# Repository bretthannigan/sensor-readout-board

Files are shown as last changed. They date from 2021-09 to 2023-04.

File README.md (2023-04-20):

# Sensor Readout Board

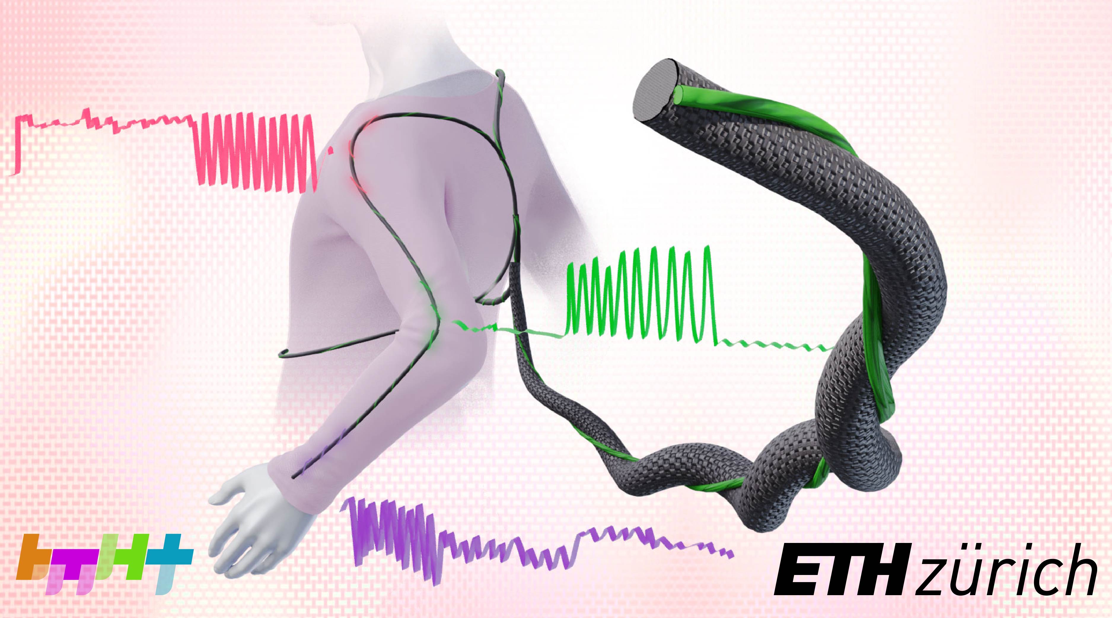
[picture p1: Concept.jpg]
Concept image


This repository includes the software, firmware, and hardware for the readout electronics used in the paper:

> B. C. Hannigan, T. J. Cuthbert, C. Admadizadeh, and C. Menon, _Distributed Sensing Along Fibres for Smart Clothing_. April 2023. [Preprint]

## Python Client

The `Client` subfolder contains the source code for the PC client, written in Python. The client allows connection to the FPGA and optional logging of data. The data can be interpreted in a variety of formats, such as:
- `raw`: raw ADC counts (32-bit signed integer)
- `iq`: impedances expressed as in-phase and quadrature components (equivalently, real and imagingary impedance components) in Ohms.
- `magphase`: impedances expressed as magnitude (in dB) and phase (in degrees).
- `RCseries`: impedances converted to resistance and capacitance values in an RC series circuit.
- `RCparallel`: impedances converted to resistance and capacitance values in an RC parallel circuit.
- `model`: (experimental) processed signals using a provided model (e.g., from sklearn or Keras) to convert the raw signals into a measure of interest.
Command-line arguments exist to control the COM port and logfile destination. One can also enable or disable the plotting of data to the screen and triggering ability. Note that the correct gain that matches the jumper on the PCB must be supplied via command-line argument for the scaling to be correct. There also exist some calibration curves as Excel spreadsheets.

## FPGA Firmware

The `Firmware` folder contains many general-purpose logic buliding blocks such as counters, FIFOs, memories, etc. and associated test-benches. The `Firmware/top` subfolder contains the top-level Verilog file `top.v` which was used for the data collection in the paper. This relies directly on the following third-party libraries:
- `verilog-lfsr` by Alex Forencich: https://github.com/alexforencich/verilog-lfsr. Used to implement the linear-feedback shift register that enables redundancy checking for the MIN protocol serial packets.
- `osdvu/uart` by Timothy Goddard: https://github.com/cyrozap/osdvu. Used to implement the UART.
- `min-protocol` by Ken Tindell: https://github.com/min-protocol/min. Used to frame the data sent to the PC.

## Hardware

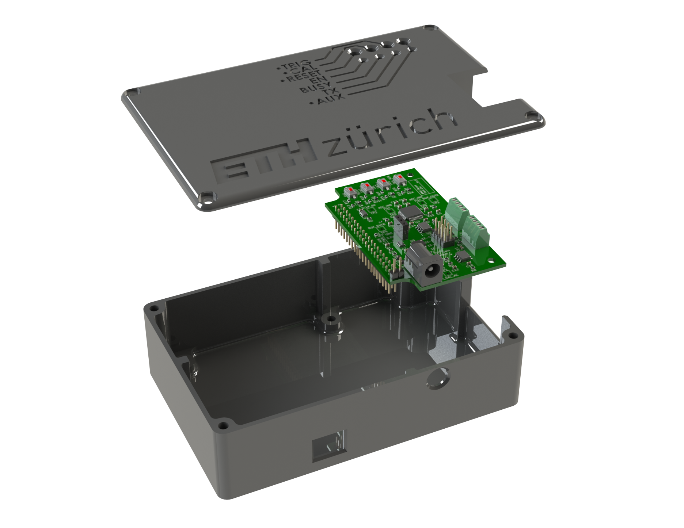
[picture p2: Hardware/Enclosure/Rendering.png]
Hardware rendering


The `Hardware/Enclosure` subfolder contains Solidworks files for the system enclosure. These were printed on a FDM 3D printer. The `Hardware/PCB` subfolder contains PCB schematic and layout files from KiCAD. The other subfolders contain (disorganized) SPICE simulations, previous iterations, and other files used during development.

©2023 ETH Zurich, Brett Hannigan; D-HEST; Biomedical and Mobile Health Technology (BMHT) Lab; Carlo Menon

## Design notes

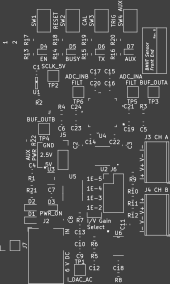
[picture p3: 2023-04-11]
Hardware/PCB/SensReadPCB-F_SilkS.png

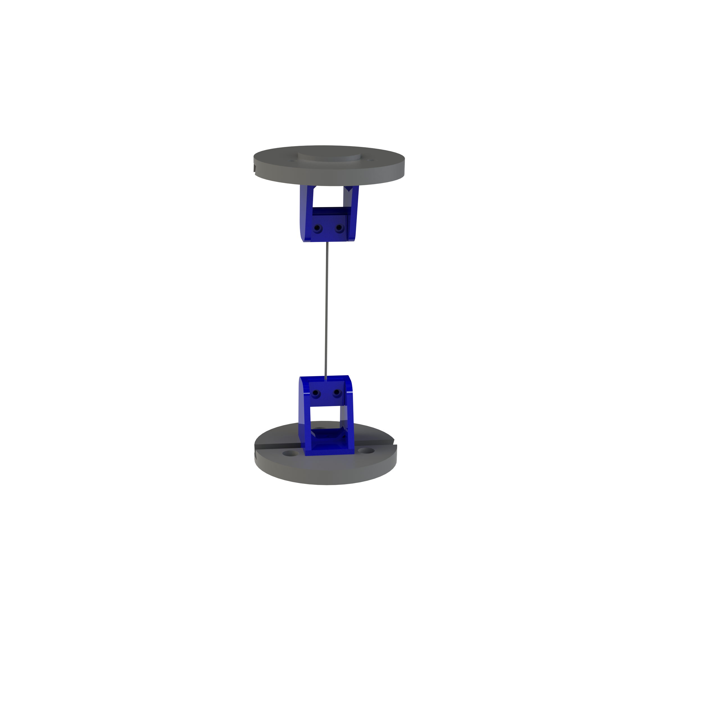
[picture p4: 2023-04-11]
Hardware/Enclosure/Single Sensor.png

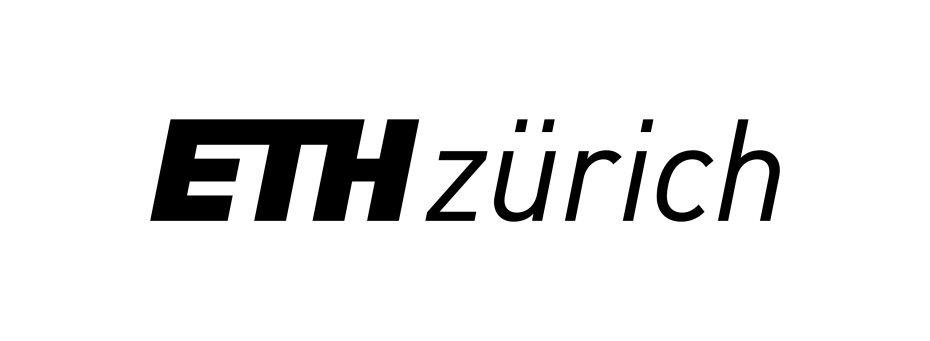
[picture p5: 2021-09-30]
Hardware/PCB/ethz.png

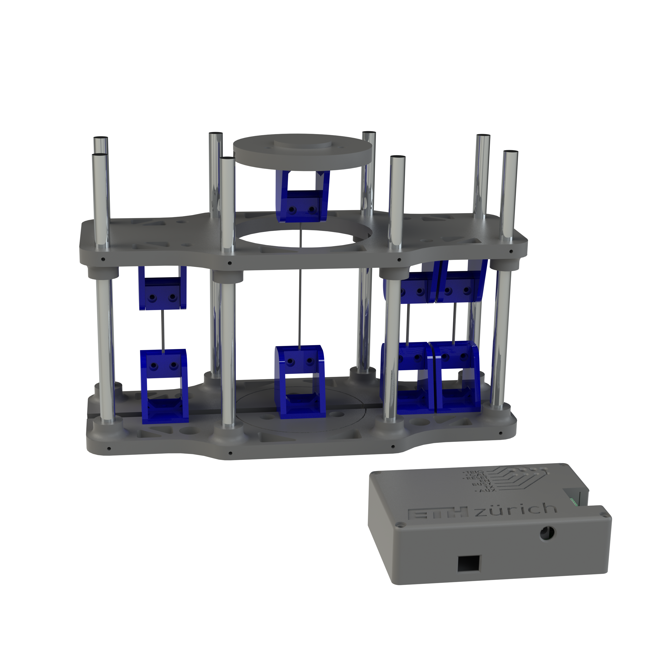
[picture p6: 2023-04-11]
Hardware/Enclosure/Rendering with Readout Enclosure.png

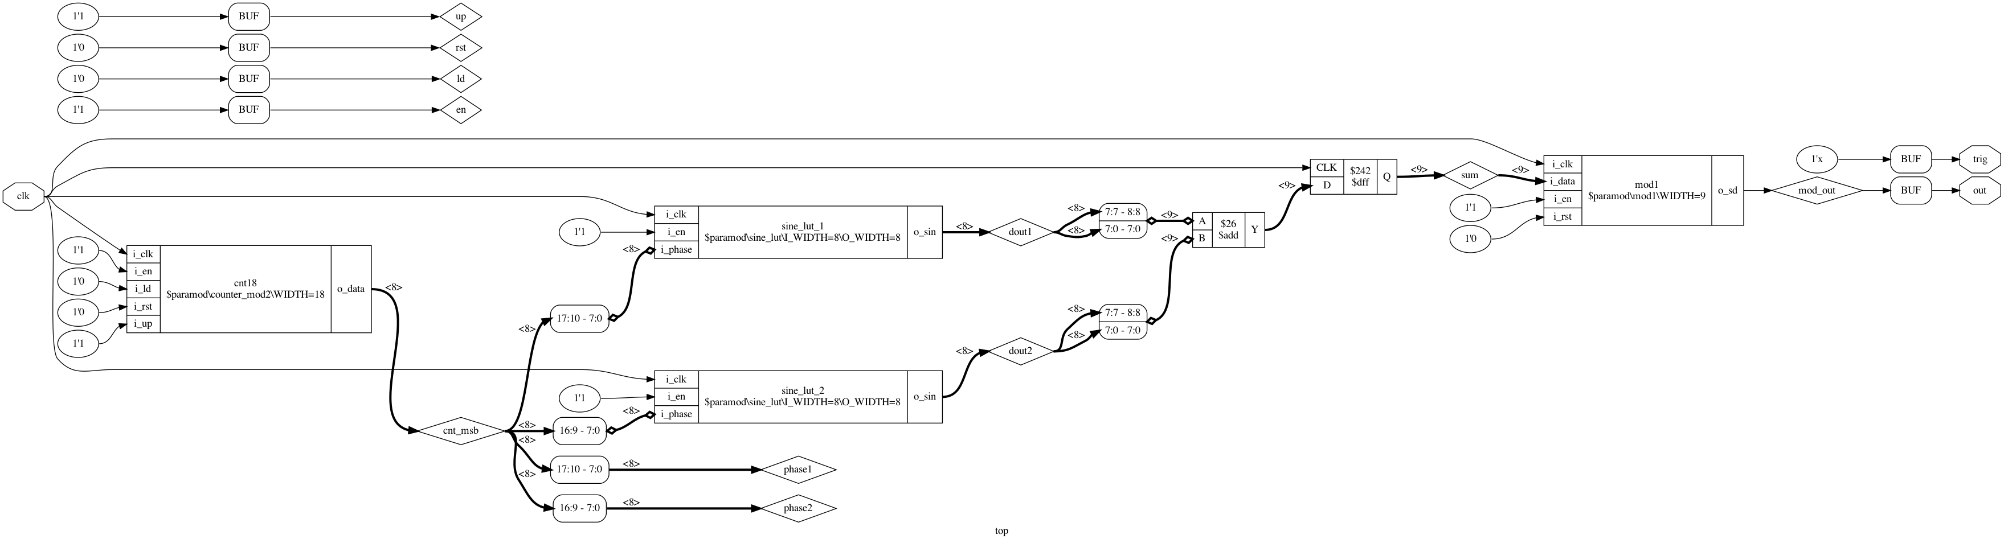
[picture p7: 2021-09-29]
Firmware/top/top.png

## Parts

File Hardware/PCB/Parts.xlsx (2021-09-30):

Electronics Assembly Product Order |  |  |  |  | 2021-09-24
Quantity | Retailer | Category | Product | Purpose | Price (ea.)
2 | Distrelec.ch | General lab | Drawer Cabinet, 36.3kg, 306x150x552mm, Raaco (https://www.distrelec.ch/en/drawer-cabinet-36-3kg-306x150x552mm-raaco-1240-123/p/18001510?q=&pos=4&origPos=4&origPageSize=50&track=true) | Parts bin organizer for electronic components. | 67.10 CHF
1 | Distrelec.ch | General lab | Precision Tweezers, Pointed, Stainless Steel 140mm, Weller Erem (https://www.distrelec.ch/en/precision-tweezers-pointed-stainless-steel-140mm-weller-erem-sssa/p/30186113) | Tweezers for general use | 17.99 CHF
1 | Distrelec.ch | General lab | SMD Tweezers, Stainless Steel, 45° Angled, 115mm, Ideal Tek (https://www.distrelec.ch/en/smd-tweezers-stainless-steel-45-angled-115mm-ideal-tek-sm103-sa/p/30101939) | Tweezers for SMD assembly | 22.83 CHF
2 | Distrelec.ch | General lab | Antistatic Adjustable Hypoallergenic Wrist Strap 10mm, Blue, RND Lab (https://www.distrelec.ch/en/antistatic-adjustable-hypoallergenic-wrist-strap-10mm-blue-rnd-lab-rnd-560-00208/p/30130388?q=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) | ESD grounding for assembly | 2.77 CHF
2 | Distrelec.ch | General lab | Coiled Earth Lead 3.05m, RND Lab (https://www.distrelec.ch/en/coiled-earth-lead-05m-rnd-lab-rnd-600-00094/p/30131945?q=&pos=3&origPos=3&origPageSize=50&track=true) | ESD grounding for assembly | 4.24 CHF
 |  |  |  |  | 189.04 CHF

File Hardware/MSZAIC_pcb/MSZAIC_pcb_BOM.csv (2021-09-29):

Reference | Value | Footprint | Datasheet | Done
U1 | LMH6619MA_NOPB | LMH6619MA:LMH6619MA&slash_NOPB |  | TRUE
R1 | 100k | Resistors_SMD:R_1206_HandSoldering | ~ | TRUE
R2 | 100k | Resistors_SMD:R_1206_HandSoldering | ~ | TRUE
R3 | 10k | Resistors_SMD:R_1206_HandSoldering | ~ | TRUE
C1 | 20p | Capacitors_SMD:C_1206_HandSoldering | ~ | TRUE
R4 | 10k | Resistors_SMD:R_1206_HandSoldering | ~ | TRUE
C2 | 20p | Capacitors_SMD:C_1206_HandSoldering | ~ | TRUE
J3 | Conn_02x04_Odd_Even | Pin_Headers:Pin_Header_Straight_2x04_Pitch2.54mm | ~ | TRUE
R5 | 10k | Resistors_SMD:R_1206_HandSoldering | ~ | TRUE
R6 | 1k | Resistors_SMD:R_1206_HandSoldering | ~ | TRUE
R7 | 100 | Resistors_SMD:R_1206_HandSoldering | ~ | TRUE
R8 | 10 | Resistors_SMD:R_1206_HandSoldering | ~ | TRUE
C9 | 100n | Capacitors_SMD:C_1206_HandSoldering | ~ | TRUE
U4 | TLE2426xD | TLE2426CD:TLE2426CD | http://www.ti.com/lit/ds/symlink/tle2426.pdf | TRUE
C11 | 1u | Capacitors_SMD:C_1206_HandSoldering | ~ | TRUE
U3 | LP2985A-10DBVR | LP2985A10DBVR:LP2985A-10DBVR |  | TRUE
C6 | 1u | Capacitors_SMD:C_1206_HandSoldering | ~ | TRUE
C10 | 10n | Capacitors_SMD:C_1206_HandSoldering | ~ | TRUE
C7 | 10n | Capacitors_SMD:C_1206_HandSoldering | ~ | TRUE
U2 | MAX903CSA+ | MAX903CSA:MAX903CSA&plus_ |  | TRUE
C4 | 100n | Capacitors_SMD:C_1206_HandSoldering | ~ | TRUE
C8 | 100n | Capacitors_SMD:C_1206_HandSoldering | ~ | TRUE
C5 | 100n | Capacitors_SMD:C_1206_HandSoldering | ~ | TRUE
C3 | 100n | Capacitors_SMD:C_1206_HandSoldering | ~ | TRUE
TP1 | DAC_AC | Measurement_Points:Measurement_Point_Square-TH_Big | ~ | #N/A
R16 | 6.98k | Resistors_SMD:R_1206_HandSoldering | ~ | TRUE
R14 | 4.64k | Resistors_SMD:R_1206_HandSoldering | ~ | TRUE
R15 | 1.10k | Resistors_SMD:R_1206_HandSoldering | ~ | TRUE
C13 | 1.5n | Capacitors_SMD:C_1206_HandSoldering | ~ | TRUE
TP6 | ADC_OUT | Measurement_Points:Measurement_Point_Square-TH_Big | ~ | #N/A
J1 | Barrel_Jack | Connectors:BARREL_JACK | ~ | TRUE
R19 | 510 | Resistors_SMD:R_1206_HandSoldering | ~ | TRUE
D4 | PWR_ON | LEDs:LED_1206_HandSoldering | ~ | TRUE
D1 | D_Schottky | Diodes_SMD:D_1206 | ~ | TRUE
D3 | D_Schottky | Diodes_SMD:D_1206 | ~ | TRUE
D6 | D_Zener | Diodes_SMD:D_1206 | ~ | TRUE
R18 | 1k | Resistors_SMD:R_1206_HandSoldering | ~ | TRUE
D2 | D_Zener | Diodes_SMD:D_1206 | ~ | TRUE
D5 | ENABLE | LEDs:LED_1206_HandSoldering | ~ | TRUE
R17 | 68 | Resistors_SMD:R_1206_HandSoldering | ~ | TRUE
R24 | 28k | Resistors_SMD:R_1206_HandSoldering | ~ | #N/A
R27 | 28k | Resistors_SMD:R_1206_HandSoldering | ~ | #N/A
C14 | 130p | Capacitors_SMD:C_1206_HandSoldering | ~ | #N/A
C16 | 130p | Capacitors_SMD:C_1206_HandSoldering | ~ | #N/A
R25 | 1.58meg | Resistors_SMD:R_1206_HandSoldering | ~ | #N/A
C15 | 130p | Capacitors_SMD:C_1206_HandSoldering | ~ | #N/A
R26 | 68.1k | Resistors_SMD:R_1206_HandSoldering | ~ | #N/A
R23 | 5.11k | Resistors_SMD:R_1206_HandSoldering | ~ | #N/A
C17 | 390p | Capacitors_SMD:C_1206_HandSoldering | ~ | #N/A
TP5 | LF_4 | Measurement_Points:Measurement_Point_Square-TH_Big | ~ | #N/A
R20 | 0R | Resistors_SMD:R_1206_HandSoldering | ~ | TRUE
R21 | 0R | Resistors_SMD:R_1206_HandSoldering | ~ | TRUE
R22 | 0 | Resistors_SMD:R_1206_HandSoldering | ~ | TRUE
R29 | 0 | Resistors_SMD:R_1206_HandSoldering | ~ | TRUE
R28 | 5.36k | Resistors_SMD:R_1206_HandSoldering | ~ | TRUE
C20 | 100n | Capacitors_SMD:C_1206_HandSoldering | ~ | TRUE
C18 | C | Capacitors_SMD:C_1206_HandSoldering | ~
TP4 | LF_3 | Measurement_Points:Measurement_Point_Square-TH_Big | ~ | #N/A
RV2 | 47k | 23BR50KLFTR:23BR50KLFTR | ~ | TRUE
C19 | 100n | Capacitors_SMD:C_1206_HandSoldering | ~ | TRUE
R10 | 13.7k | Resistors_SMD:R_1206_HandSoldering | ~ | TRUE
TP3 | LF_2 | Measurement_Points:Measurement_Point_Square-TH_Big | ~ | #N/A
TP2 | LF_1 | Measurement_Points:Measurement_Point_Square-TH_Big | ~ | #N/A
RV1 | 10k | 23BR50KLFTR:23BR50KLFTR | ~ | TRUE
R13 | 806 | Resistors_SMD:R_1206_HandSoldering | ~ | TRUE
R12 | 750 | Resistors_SMD:R_1206_HandSoldering | ~ | TRUE
R11 | 14.0k | Resistors_SMD:R_1206_HandSoldering | ~ | TRUE
C12 | 680p | Capacitors_SMD:C_1206_HandSoldering | ~ | TRUE
R9 | 4.75k | Resistors_SMD:R_1206_HandSoldering | ~ | TRUE
U5 | LM6144AIM_NOPB | LM6144AIM:LM6144AIM&slash_NOPB |  | TRUE
TP8 | TestPoint | Measurement_Points:Measurement_Point_Square-TH_Big | ~ | #N/A
TP7 | TestPoint | Measurement_Points:Measurement_Point_Square-TH_Big | ~ | #N/A
J4 | Screw_Terminal_01x04 | TerminalBlocks_Phoenix:TerminalBlock_Phoenix_MPT-2.54mm_4pol | ~ | TRUE
J2 | Conn_02x20_Odd_Even | Pin_Headers:Pin_Header_Straight_2x20_Pitch2.54mm | ~ | TRUE
 |  |  |  | 56

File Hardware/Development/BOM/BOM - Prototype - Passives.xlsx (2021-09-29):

Howland Current Source
Label | Type | Value
R1 | Resistor | 100 kΩ | *must be matched
R2 | Resistor | 100 kΩ | *must be matched
R3 | Resistor | 10 kΩ | **must be matched
R4 | Resistor | 10 kΩ | **must be matched
C1 | Capacitor | 20 pF
C2 | Capacitor | 20 pF
ADC Stage 1
Label | Type | Value
R1 | Resistor | 56.2 kΩ
R2 | Resistor | 90 kΩ
R3 | Resistor | 261 kΩ
R4 | Resistor | 2.32 kΩ
R5 | Resistor | 2.47 kΩ
R6 | Resistor | 95.3kΩ
R7 | Resistor | 16.5 kΩ
R8 | Resistor | 280 kΩ
C1 | Capacitor | 200 pF
C2 | Capacitor | 200 pF
ADC Stage 2
Label | Type | Value
R1 | Resistor | 1.58 MΩ
R2 | Resistor | 5.36 kΩ
R3 | Resistor | 5.11 kΩ
R4 | Resistor | 68.1kΩ
R5 | Resistor | 28 kΩ | *must be matched
R6 | Resistor | 28 kΩ | *must be matched
C1 | Capacitor | 390 pF
C2 | Capacitor | 130 pF
C3 | Capacitor | 130 pF | **must be matched
C4 | Capacitor | 130 pF | **must be matched
Extras
Decoupling capacitors 100 nF
Various test resistances, 100 Ω - 50 kΩ
Various test capacitors in the pF range

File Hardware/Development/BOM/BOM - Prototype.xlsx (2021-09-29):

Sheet: Sheet1
Howland Current Source
Label | Type | Value/Part Number
R1 | Resistor | 100 kΩ | *must be matched | l
R2 | Resistor | 100 kΩ | *must be matched | l
R3 | Resistor | 10 kΩ | **must be matched | l
R4 | Resistor | 10 kΩ | **must be matched | l
C1 | Capacitor | 20 pF |  | l
C2 | Capacitor | 20 pF |  | l
U1 | Op-amp | OPA350PA |  | l
U2 | Op-amp | OPA350PA |  | l
U3 | Voltage reference | TLE2426CP |  | l
ADC Loop filter
Label | Type |  | Value
R1 | Resistor |  | 14.0 kΩ | l
R2 | Resistor |  | 1.10 kΩ | l
R3 | Resistor |  | 4.64 kΩ | l
R4 | Resistor |  | 4.75 kΩ | l
R5 | Resistor |  | 6.98 kΩ | l
R6 | Resistor |  | 13.7 kΩ | l
R7 | Resistor |  | 750 Ω | l
R8 | Resistor |  | 806 Ω | l
C1 | Capacitor |  | 680 pF
C2 | Capacitor |  | 1.5 nF
Extras
Decoupling capacitors 100 nF |  |  |  | l
Various test resistances, 100 Ω - 50 kΩ |  |  |  | l
Various test capacitors in the pF range |  |  |  | l

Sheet: 2021-02-04
ADC Loop filter | Stage 1
Label | Type | Value | Ordered | Notes
R1 | Resistor | 11.3k | TRUE
R2 | Resistor | 11.8k | TRUE
R3 | Resistor | 9.09k | TRUE
R4 | Resistor | 9.76k | TRUE
R5 | Resistor | 24.9k | TRUE
R6 | Resistor | 16.2k | TRUE
R7 | Resistor | 2.61k | TRUE
R8 | Resistor | 5.11k | TRUE
C1 | Capacitor | 160p | TRUE | 150p instead
C2 | Capacitor | 160p | TRUE | 150p instead
ADC Loop filter | Stage 2
Label | Type | Value | Ordered | Notes
R1 | Resistor | 243k | TRUE
R2 | Resistor | 5.23k | TRUE
R3 | Resistor | 1.30k | TRUE
R4 | Resistor | 46.4k | TRUE
R5 | Resistor | 5.62k | TRUE
R6 | Resistor | 5.62k | TRUE
C1 | Capacitor | 220p | TRUE
C2 | Capacitor | 22p | TRUE
C3 | Capacitor | 100p | TRUE
C4 | Capacitor | 100p | TRUE
Missed from last order
R13 | Resistor | 806 | TRUE

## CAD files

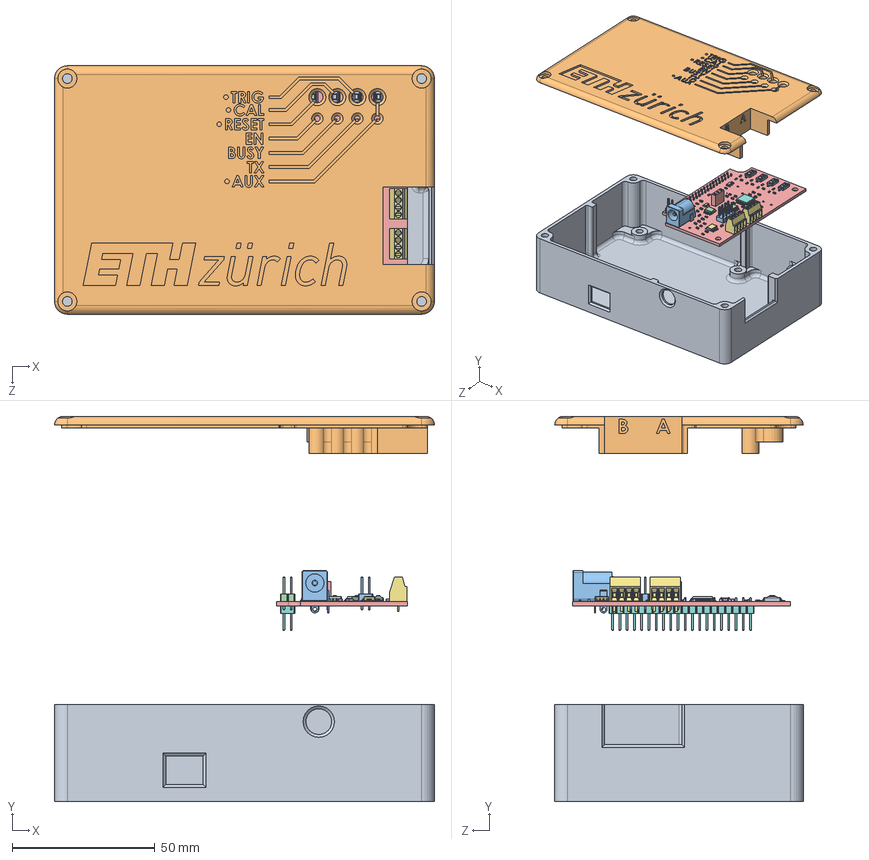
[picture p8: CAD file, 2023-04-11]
Hardware/Enclosure/Enclosure.SLDASM
133.0 x 134.9 x 87.0 mm
EnclosureBase
EnclosureLid
SOLID.step x 2
SOLID-0.step
SOLID-1.step
SOLID-2.step x 24
SOLID-3.step x 2
SOLID-4.step
SOLID-5.step x 22
SOLID-6.step x 5
SOLID-7.step
SOLID-8.step
COMPOUND.step
COMPOUND-9.step
COMPOUND-10.step
COMPOUND-11.step
COMPOUND-12.step x 4
COMPOUND-13.step
SOLID-14.step
COMPOUND-15.step
COMPOUND-16.step

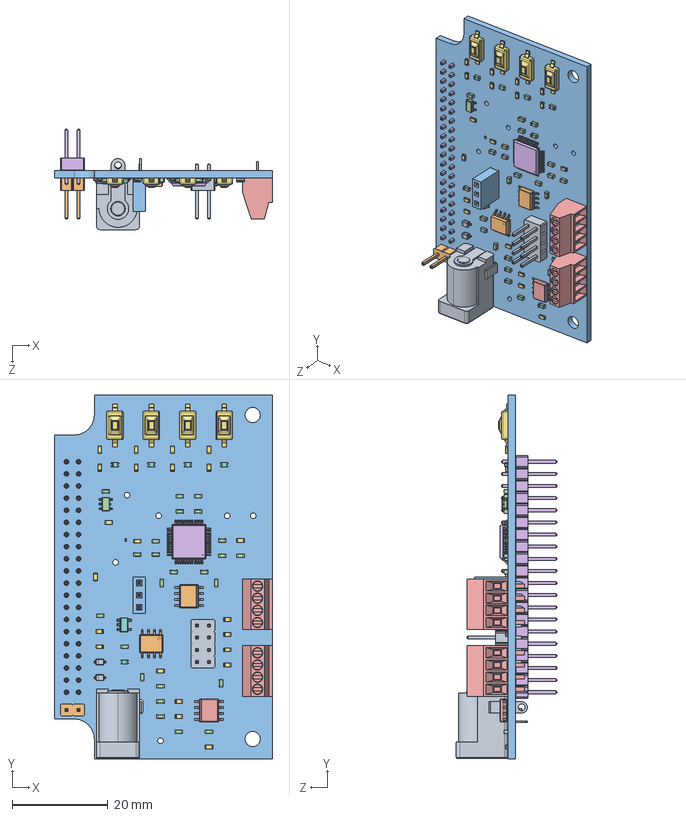
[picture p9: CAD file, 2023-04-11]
Hardware/Enclosure/SensReadPCB.SLDASM
45.7 x 76.2 x 21.0 mm
SOLID.step x 2
SOLID-0.step
SOLID-1.step
SOLID-2.step x 24
SOLID-3.step x 2
SOLID-4.step
SOLID-5.step x 22
SOLID-6.step x 5
SOLID-7.step
SOLID-8.step
COMPOUND.step
COMPOUND-9.step
COMPOUND-10.step
COMPOUND-11.step
COMPOUND-12.step x 4
COMPOUND-13.step
SOLID-14.step
COMPOUND-15.step
COMPOUND-16.step

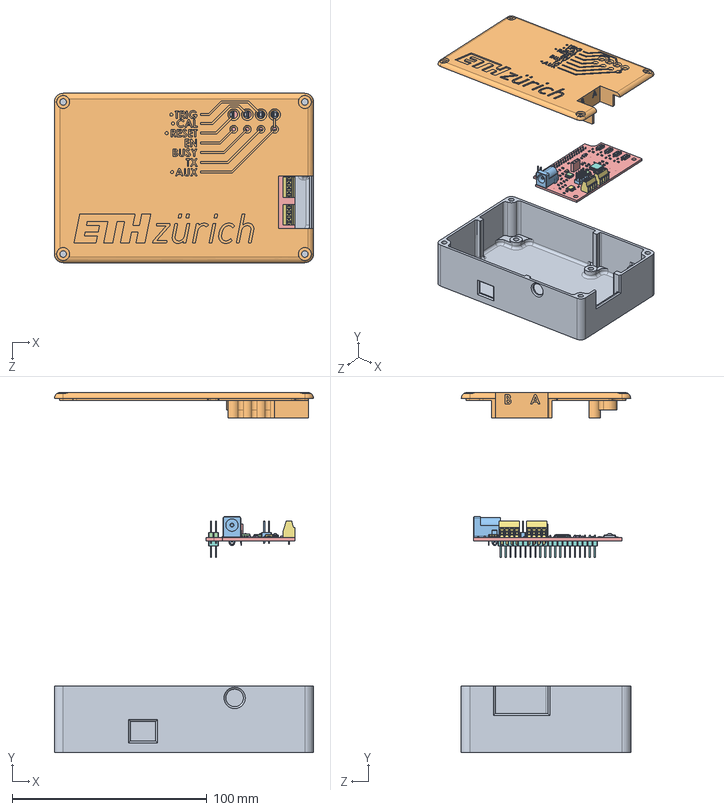
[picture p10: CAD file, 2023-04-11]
Hardware/Enclosure/Backup of Enclosure.SLDASM
133.0 x 184.7 x 87.0 mm
EnclosureBase
EnclosureLid
SOLID.step x 2
SOLID-0.step
SOLID-1.step
SOLID-2.step x 24
SOLID-3.step x 2
SOLID-4.step
SOLID-5.step x 22
SOLID-6.step x 5
SOLID-7.step
SOLID-8.step
COMPOUND.step
COMPOUND-9.step
COMPOUND-10.step
COMPOUND-11.step
COMPOUND-12.step x 4
COMPOUND-13.step
SOLID-14.step
COMPOUND-15.step
COMPOUND-16.step

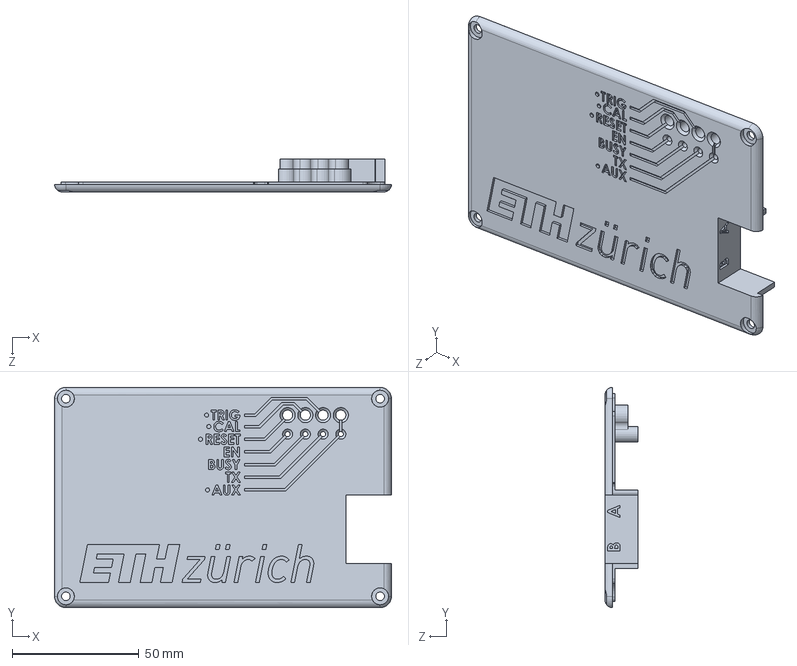
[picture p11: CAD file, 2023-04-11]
Hardware/Enclosure/EnclosureLid.sldprt
133.0 x 87.0 x 13.0 mm

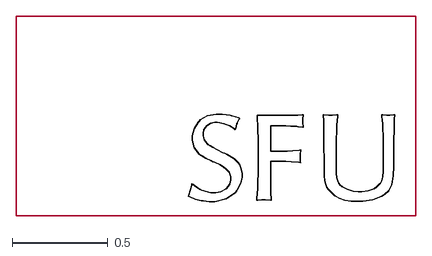
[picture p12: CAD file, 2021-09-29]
Hardware/MSZAIC_pcb/SFU-block-logo.dxf
2.08 x 1.04

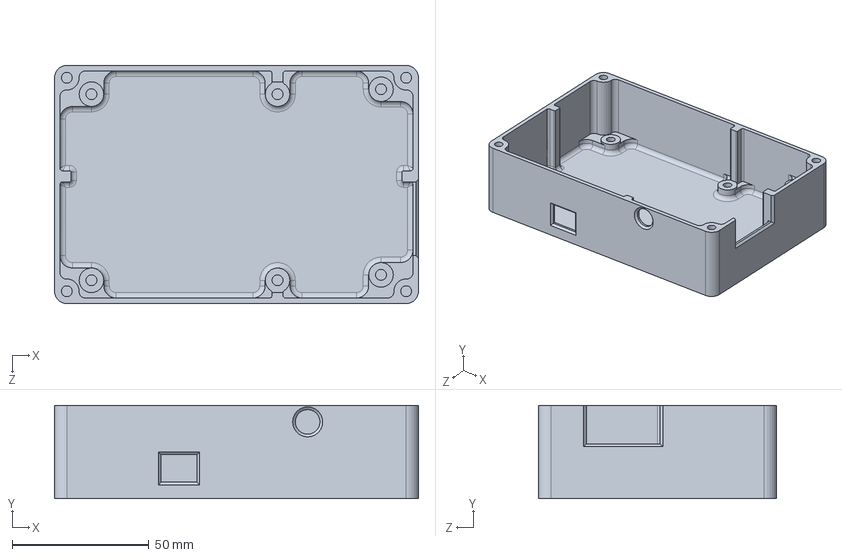
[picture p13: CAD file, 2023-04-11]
Hardware/Enclosure/EnclosureBase.SLDPRT
133.0 x 34.0 x 87.0 mm

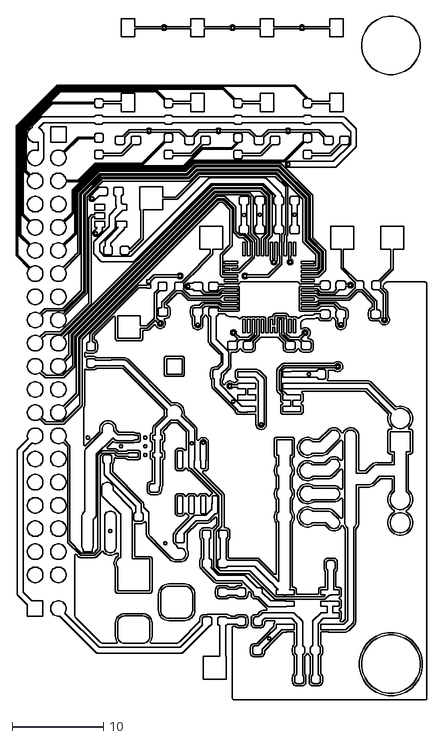
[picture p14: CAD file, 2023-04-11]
Hardware/PCB/SensReadPCB-F_Cu.dxf
45.0 x 74.9

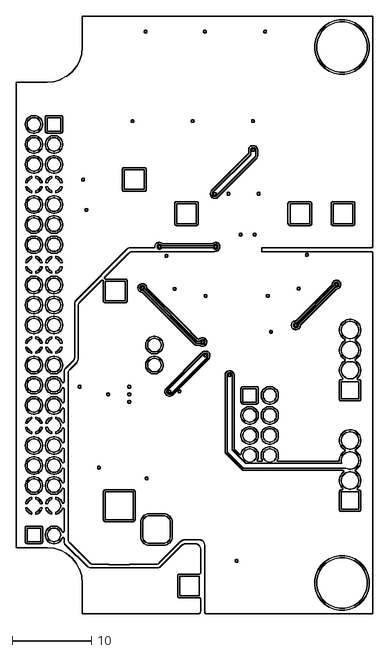
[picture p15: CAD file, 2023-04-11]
Hardware/PCB/SensReadPCB-B_Cu.dxf
45.2 x 75.6

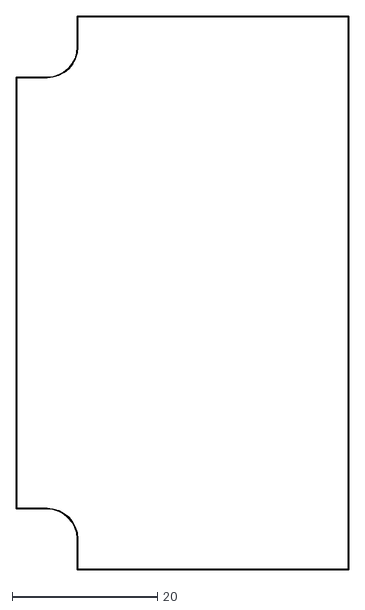
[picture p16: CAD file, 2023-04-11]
Hardware/PCB/SensReadPCB-Edge_Cuts.dxf
45.8 x 76.3

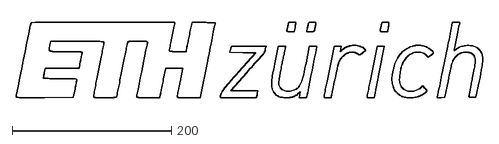
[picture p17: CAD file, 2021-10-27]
Hardware/Enclosure/ethz.dxf
584.9 x 95.1

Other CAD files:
Firmware/sine_lut/sintable.obj
Hardware/PCB/sensreadpcb.wrl_2.sldprt
Hardware/PCB/SensReadPCB.FCStd
Hardware/Enclosure/EnclosureLid - EnclosureBase-1.STL
Hardware/Enclosure/EnclosureLid - EnclosureLid-1.STL
Hardware/Enclosure/BH1BoardEnclosure.STL
Hardware/Enclosure/BH2EnclosureBase.STL
Hardware/Enclosure/Backup of EnclosureLid.sldprt
Hardware/Enclosure/BH3EnclosureLid.STL
Hardware/Enclosure/BH4EnclosureLid.STL
Hardware/Enclosure/Backup of EnclosureBase.SLDPRT
Hardware/Enclosure/EnclosureBase.SLDDRW
Hardware/PCB/SensReadPCB-B_Mask.dxf
Hardware/PCB/SensReadPCB-B_Paste.dxf
Hardware/PCB/SensReadPCB-B_SilkS.dxf
Hardware/PCB/SensReadPCB-F_Mask.dxf
Hardware/PCB/SensReadPCB-F_Paste.dxf

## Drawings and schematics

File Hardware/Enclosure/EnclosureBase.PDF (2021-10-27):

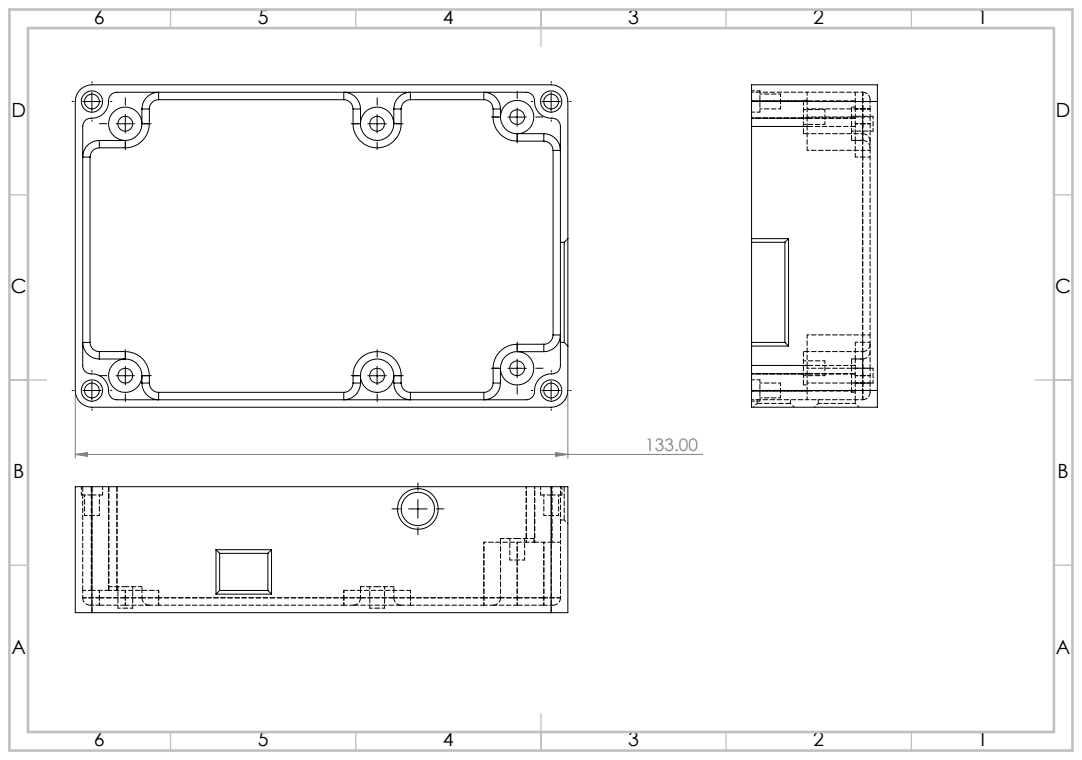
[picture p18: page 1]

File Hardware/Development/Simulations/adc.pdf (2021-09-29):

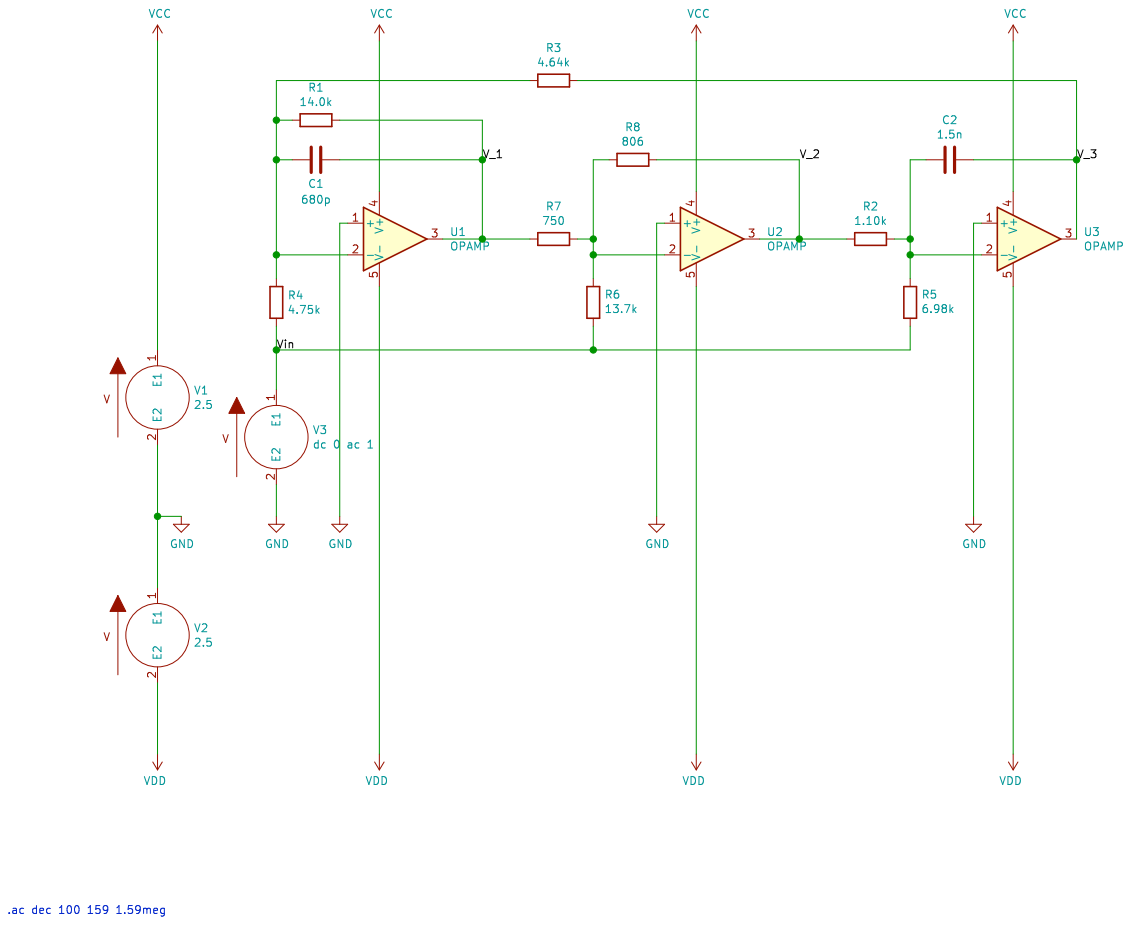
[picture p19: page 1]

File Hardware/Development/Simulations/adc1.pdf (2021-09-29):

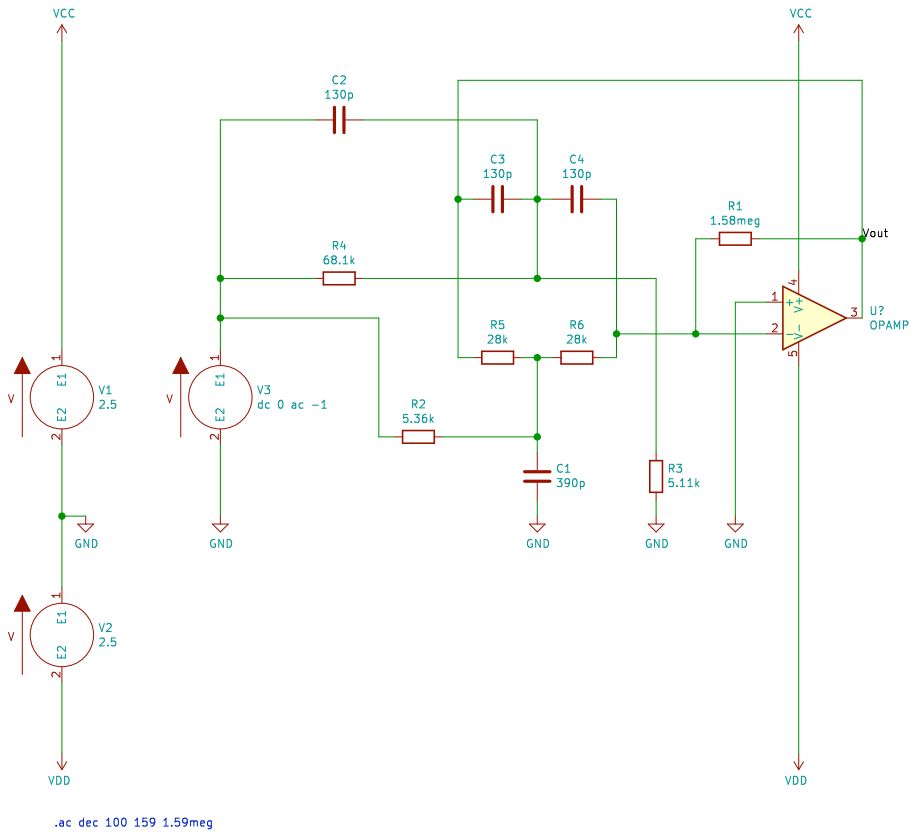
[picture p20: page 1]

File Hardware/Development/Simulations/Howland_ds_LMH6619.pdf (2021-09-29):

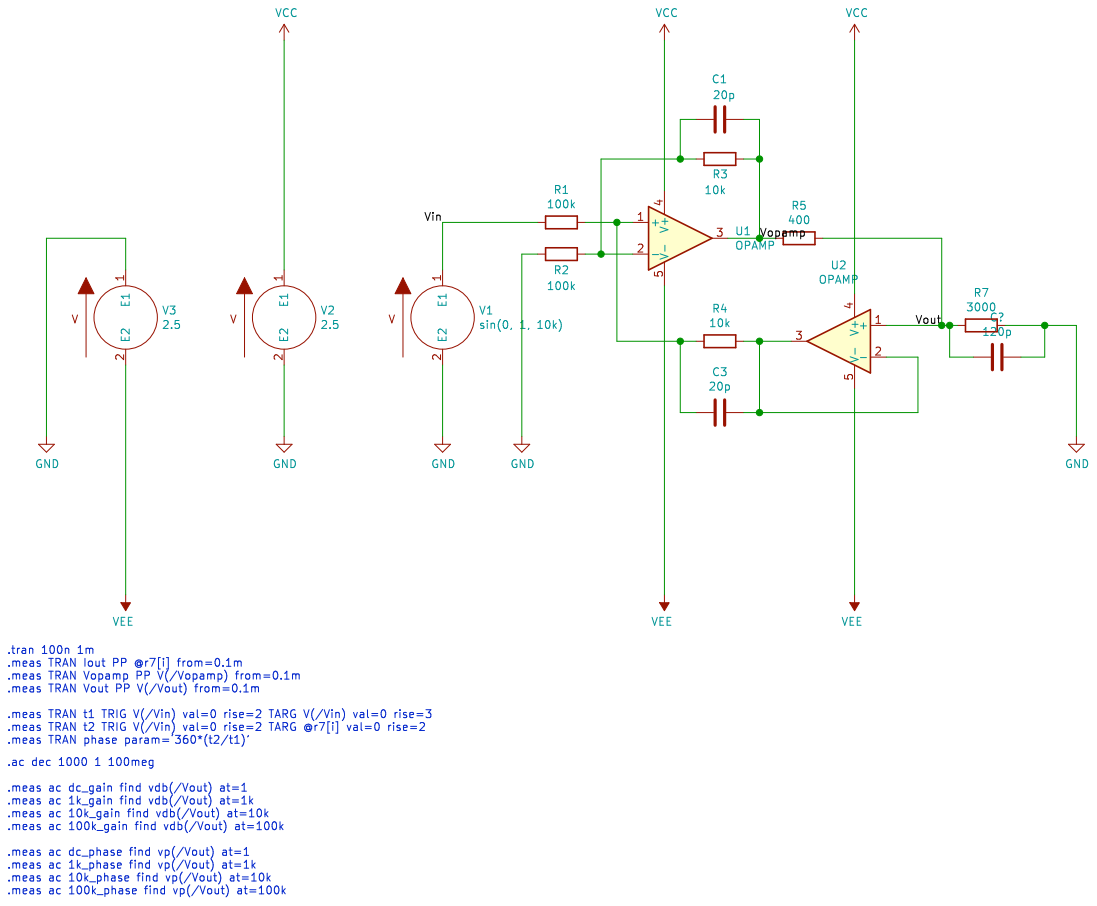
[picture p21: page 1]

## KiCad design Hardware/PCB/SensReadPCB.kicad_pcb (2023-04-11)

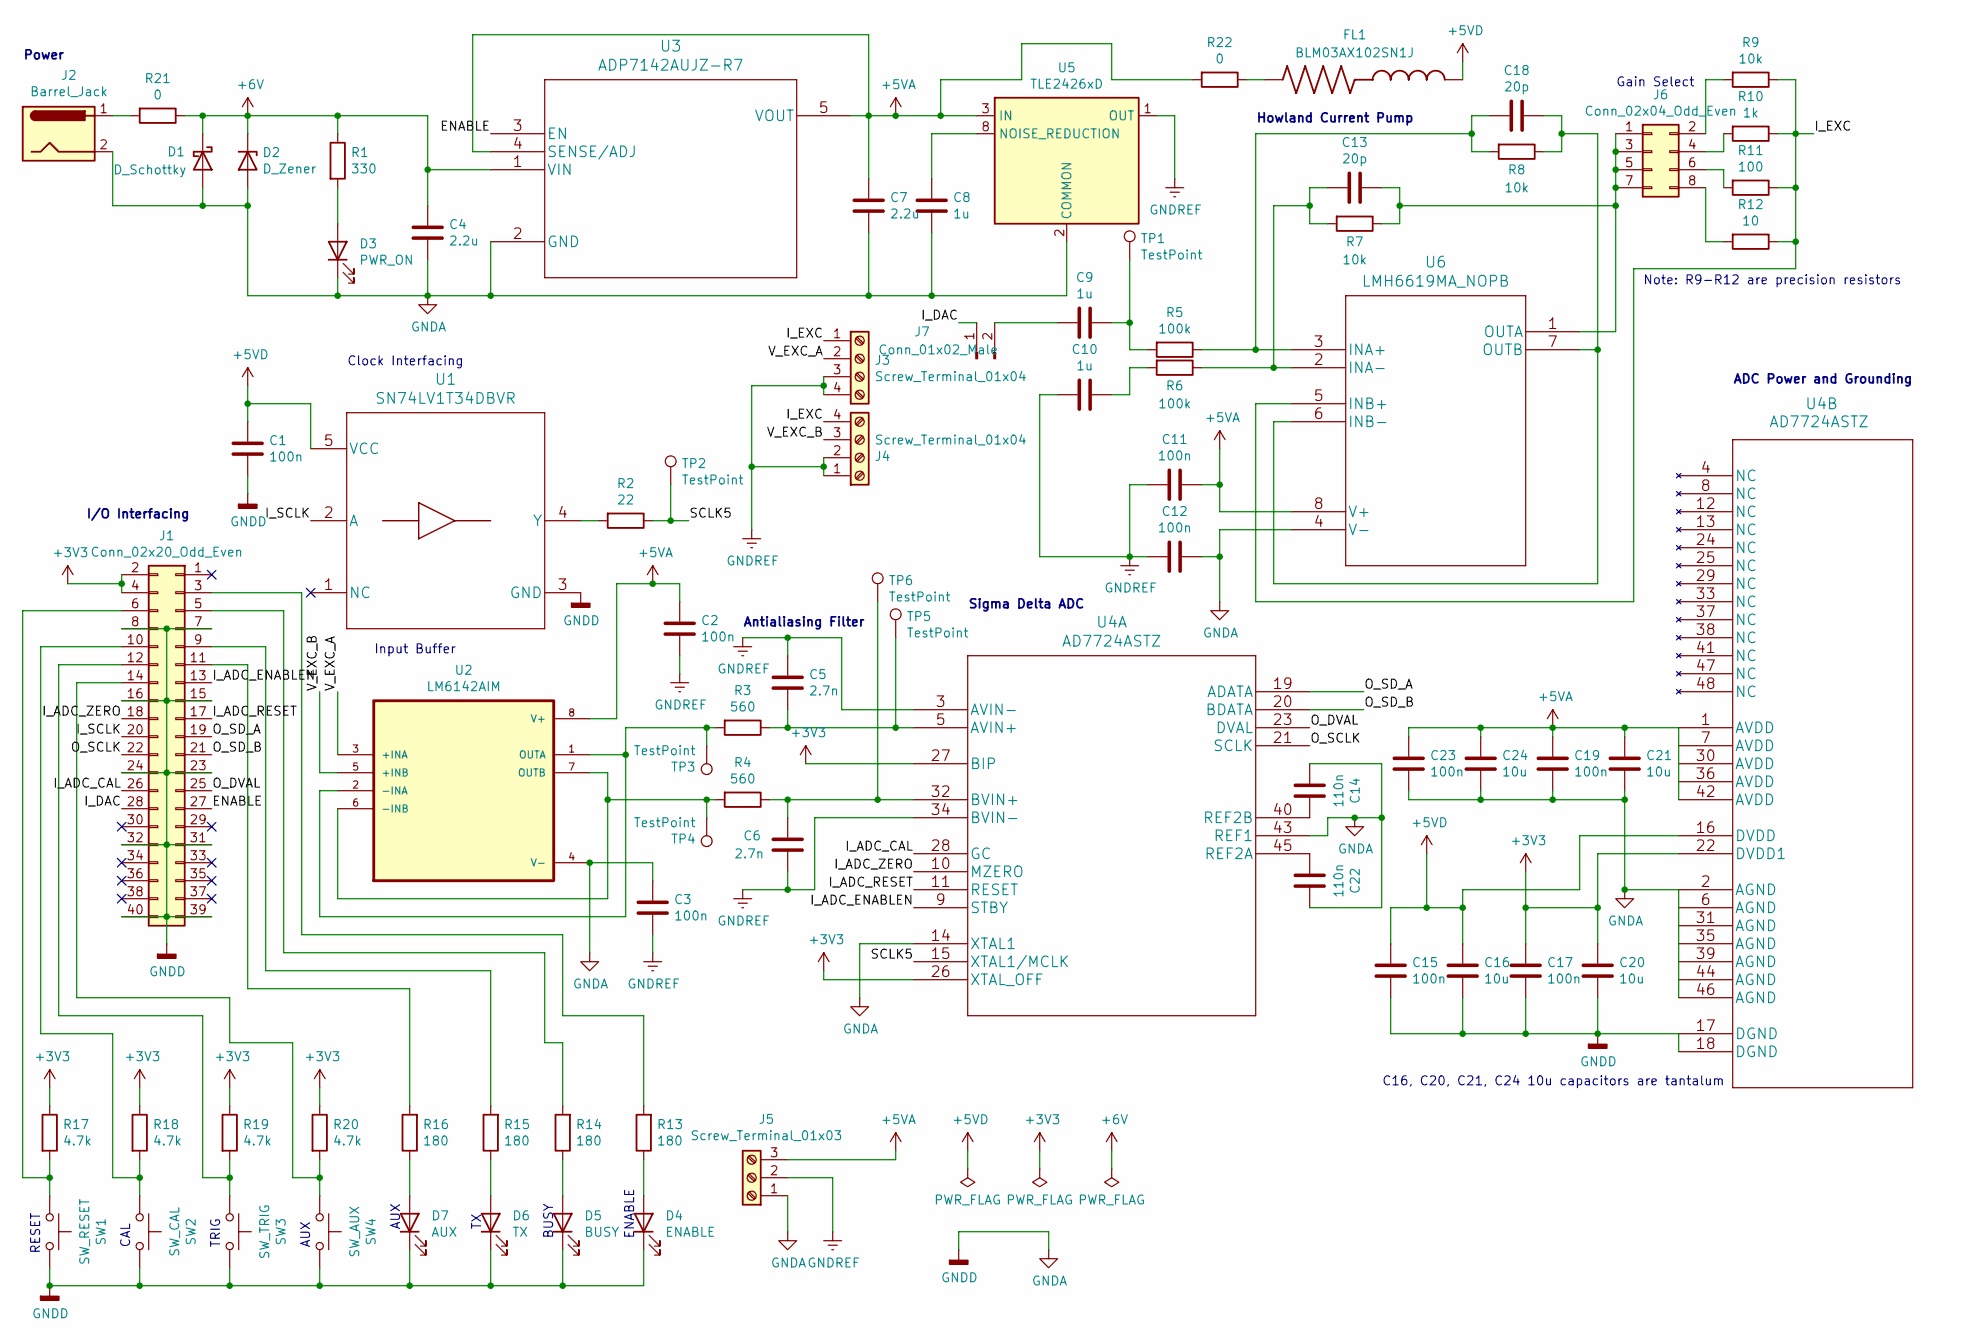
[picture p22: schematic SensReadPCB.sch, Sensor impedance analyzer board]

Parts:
C1, C2, C3, C11, C12, C15, C17, C19, C23: 100n; C_0603_1608Metric_Pad1.08x0.95mm_HandSolder
C4, C7: 2.2u; C_0603_1608Metric_Pad1.08x0.95mm_HandSolder
C5, C6: 2.7n; C_0603_1608Metric_Pad1.08x0.95mm_HandSolder
C8, C9, C10: 1u; C_0603_1608Metric_Pad1.08x0.95mm_HandSolder
C13, C18: 20p; C_0603_1608Metric_Pad1.08x0.95mm_HandSolder
C14, C22: 110n; C_0603_1608Metric_Pad1.08x0.95mm_HandSolder
C16, C20, C21, C24: 10u; C_0603_1608Metric_Pad1.08x0.95mm_HandSolder
D1: D_Schottky; D_SOD-323_HandSoldering
D2: D_Zener; D_SOD-323_HandSoldering
D3: PWR_ON; D_0603_1608Metric_Pad1.05x0.95mm_HandSolder
D4: ENABLE; D_0603_1608Metric_Pad1.05x0.95mm_HandSolder
D5: BUSY; D_0603_1608Metric_Pad1.05x0.95mm_HandSolder
D6: TX; D_0603_1608Metric_Pad1.05x0.95mm_HandSolder
D7: AUX; D_0603_1608Metric_Pad1.05x0.95mm_HandSolder
FL1: BLM03AX102SN1J; BEADC0603X33N
J1: Conn_02x20_Odd_Even; PinHeader_2x20_P2.54mm_Vertical
J2: Barrel_Jack; KLDX-0202-A
J3, J4: Screw_Terminal_01x04; TerminalBlock_Phoenix_MPT-0,5-4-2.54_1x04_P2.54mm_Horizontal
J5: Screw_Terminal_01x03; PinSocket_1x03_P2.54mm_Vertical
J6: Conn_02x04_Odd_Even; PinHeader_2x04_P2.54mm_Vertical
J7: Conn_01x02_Male; PinHeader_1x02_P2.54mm_Vertical
R1: 330; R_0603_1608Metric_Pad0.98x0.95mm_HandSolder
R2: 22; R_0603_1608Metric_Pad0.98x0.95mm_HandSolder
R3, R4: 560; R_0603_1608Metric_Pad0.98x0.95mm_HandSolder
R5, R6: 100k; R_0603_1608Metric_Pad0.98x0.95mm_HandSolder
R7, R8, R9: 10k; R_0603_1608Metric_Pad0.98x0.95mm_HandSolder
R10: 1k; R_0603_1608Metric_Pad0.98x0.95mm_HandSolder
R11: 100; R_0603_1608Metric_Pad0.98x0.95mm_HandSolder
R12: 10; R_0603_1608Metric_Pad0.98x0.95mm_HandSolder
R13, R14, R15, R16: 180; R_0603_1608Metric_Pad0.98x0.95mm_HandSolder
R17, R18, R19, R20: 4.7k; R_0603_1608Metric_Pad0.98x0.95mm_HandSolder
R21, R22: 0; R_0603_1608Metric_Pad0.98x0.95mm_HandSolder
SW1: SW_RESET; PTS636_SMTR
SW2: SW_CAL; PTS636_SMTR
SW3: SW_TRIG; PTS636_SMTR
SW4: SW_AUX; PTS636_SMTR
TP1, TP2, TP3, TP4, TP5, TP6: TestPoint; TestPoint_THTPad_2.5x2.5mm_Drill1.2mm
U1: SN74LV1T34DBVR
U2: LM6142AIM
U3: ADP7142AUJZ-R7
U4: AD7724ASTZ
U5: TLE2426xD; SOIC-8_3.9x4.9mm_P1.27mm
U6: LMH6619MA_NOPB; LMH6619MA

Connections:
+3V3: C17.1, C20.1, J1.2, J1.4, R17.1, R18.1, R19.1, R20.1, U4.22 (DVDD1), U4.26 (XTAL_OFF), U4.27 (BIP)
+5VA: C2.1, C7.1, C11.1, C19.1, C21.1, C23.1, C24.1, J5.3, R22.2, U2.8 (V+), U3.4 (SENSE/ADJ), U3.5 (VOUT), U4.1 (AVDD), U4.7 (AVDD), U4.30 (AVDD), U4.36 (AVDD), U4.42 (AVDD), U5.3 (IN), U6.8 (V+)
+5VD: C1.1, C15.1, C16.1, FL1.1, U1.5 (VCC), U4.16 (DVDD)
+6V: C4.1, D1.1 (K), D2.1 (K), R1.1, R21.1, U3.1 (VIN)
/ENABLE: J1.27, U3.3 (EN)
/I_ADC_CAL: J1.26, U4.28 (GC)
/I_ADC_ENABLEN: J1.13, U4.9 (STBY)
/I_ADC_RESET: J1.17, U4.11 (RESET)
/I_ADC_ZERO: J1.18, U4.10 (MZERO)
/I_DAC: J1.28, J7.1
/I_EXC: J3.1, J4.4, R9.1, R10.1, R11.1, R12.1, U6.5 (INB+)
/I_SCLK: J1.20, U1.2 (A)
/O_DVAL: J1.25, U4.23 (DVAL)
/O_SCLK: J1.22, U4.21 (SCLK)
/O_SD_A: J1.19, U4.19 (ADATA)
/O_SD_B: J1.21, U4.20 (BDATA)
/SCLK5: R2.1, TP2.1, U4.15 (XTAL1/MCLK)
/V_EXC_A: J3.2, U2.3 (+INA)
/V_EXC_B: J4.3, U2.5 (+INB)
GNDA: C1.2, C3.1, C4.2, C7.2, C8.2, C12.1, C14.2, C15.2, C16.2, C17.2, C19.2, C20.2, C21.2, C22.1, C23.2, C24.2, D1.2 (A), D2.2 (A), D3.1 (K), D4.1 (K), D5.1 (K), D6.1 (K), D7.1 (K), J1.7, J1.8, J1.15, J1.16, J1.23, J1.24, J1.31, J1.32, J1.39, J1.40, J2.2, J5.1, SW1.2, SW2.2, SW3.2, SW4.2, U1.3 (GND), U2.4 (V-), U3.2 (GND), U4.2 (AGND), U4.6 (AGND), U4.14 (XTAL1), U4.17 (DGND), U4.18 (DGND), U4.31 (AGND), U4.35 (AGND), U4.39 (AGND), U4.43 (REF1), U4.44 (AGND), U4.46 (AGND), U5.2 (COMMON), U6.4 (V-)
GNDREF: C2.2, C3.2, C5.1, C6.2, C10.2, C11.2, C12.2, J3.3, J3.4, J4.1, J4.2, J5.2, U4.3 (AVIN-), U4.34 (BVIN-), U5.1 (OUT)
unnamed: C5.2, R3.1, TP5.1, U4.5 (AVIN+)
unnamed: C6.1, R4.1, TP6.1, U4.32 (BVIN+)
unnamed: C8.1, U5.8 (NOISE_REDUCTION)
unnamed: C9.1, R5.2, TP1.1
unnamed: C9.2, J7.2
unnamed: C10.1, R6.2
unnamed: C13.1, J6.1, J6.3, J6.5, J6.7, R7.1, U6.1 (OUTA)
unnamed: C13.2, R6.1, R7.2, U6.2 (INA-)
unnamed: C14.1, U4.40 (REF2B)
unnamed: C18.1, R8.1, U6.6 (INB-), U6.7 (OUTB)
unnamed: C18.2, R5.1, R8.2, U6.3 (INA+)
unnamed: C22.2, U4.45 (REF2A)
unnamed: D3.2 (A), R1.2
unnamed: D4.2 (A), R13.1
unnamed: D5.2 (A), R14.1
unnamed: D6.2 (A), R15.1
unnamed: D7.2 (A), R16.1
unnamed: FL1.2, R22.1
unnamed: J1.3, R13.2
unnamed: J1.5, R14.2
unnamed: J1.6, R17.2, SW1.1
unnamed: J1.9, R15.2
unnamed: J1.10, R18.2, SW2.1
unnamed: J1.11, R16.2
unnamed: J1.12, R19.2, SW3.1
unnamed: J1.14, R20.2, SW4.1
unnamed: J2.1, R21.2
unnamed: J6.2, R9.2
unnamed: J6.4, R10.2
unnamed: J6.6, R11.2
unnamed: J6.8, R12.2
unnamed: R2.2, U1.4 (Y)
unnamed: R3.2, TP3.1, U2.1 (OUTA), U2.2 (-INA)
unnamed: R4.2, TP4.1, U2.6 (-INB), U2.7 (OUTB)

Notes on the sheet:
Sigma Delta ADC
Antialiasing Filter
ADC Power and Grounding
Howland Current Pump
Power
Clock Interfacing
Input Buffer
I/O Interfacing
Note: R9-R12 are precision resistors
ENABLE
BUSY
TRIG
CAL
RESET
AUX
Gain Select
C16, C20, C21, C24 10u capacitors are tantalum

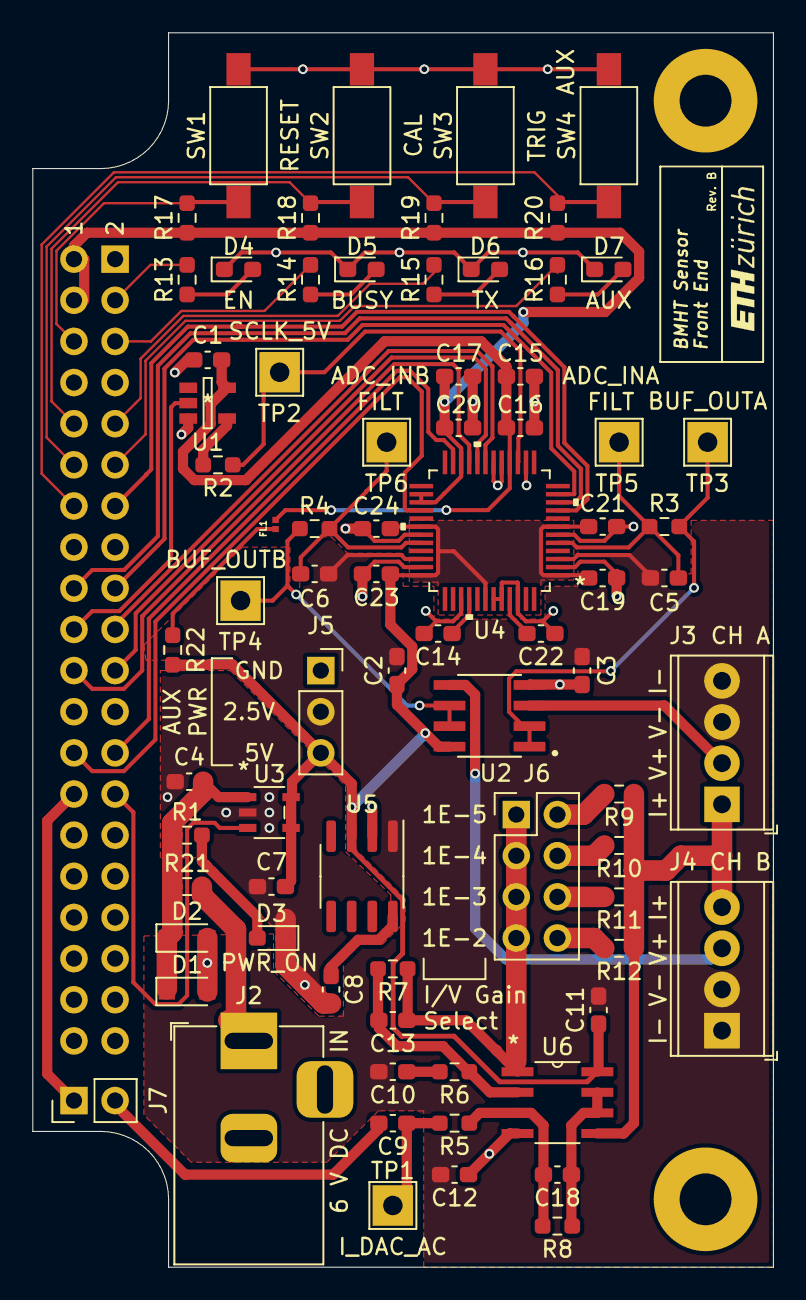
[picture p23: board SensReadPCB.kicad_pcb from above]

Board: 2 copper layers, 45.7 x 76.2 mm, 77 parts (1 on the bottom side), 55 nets.

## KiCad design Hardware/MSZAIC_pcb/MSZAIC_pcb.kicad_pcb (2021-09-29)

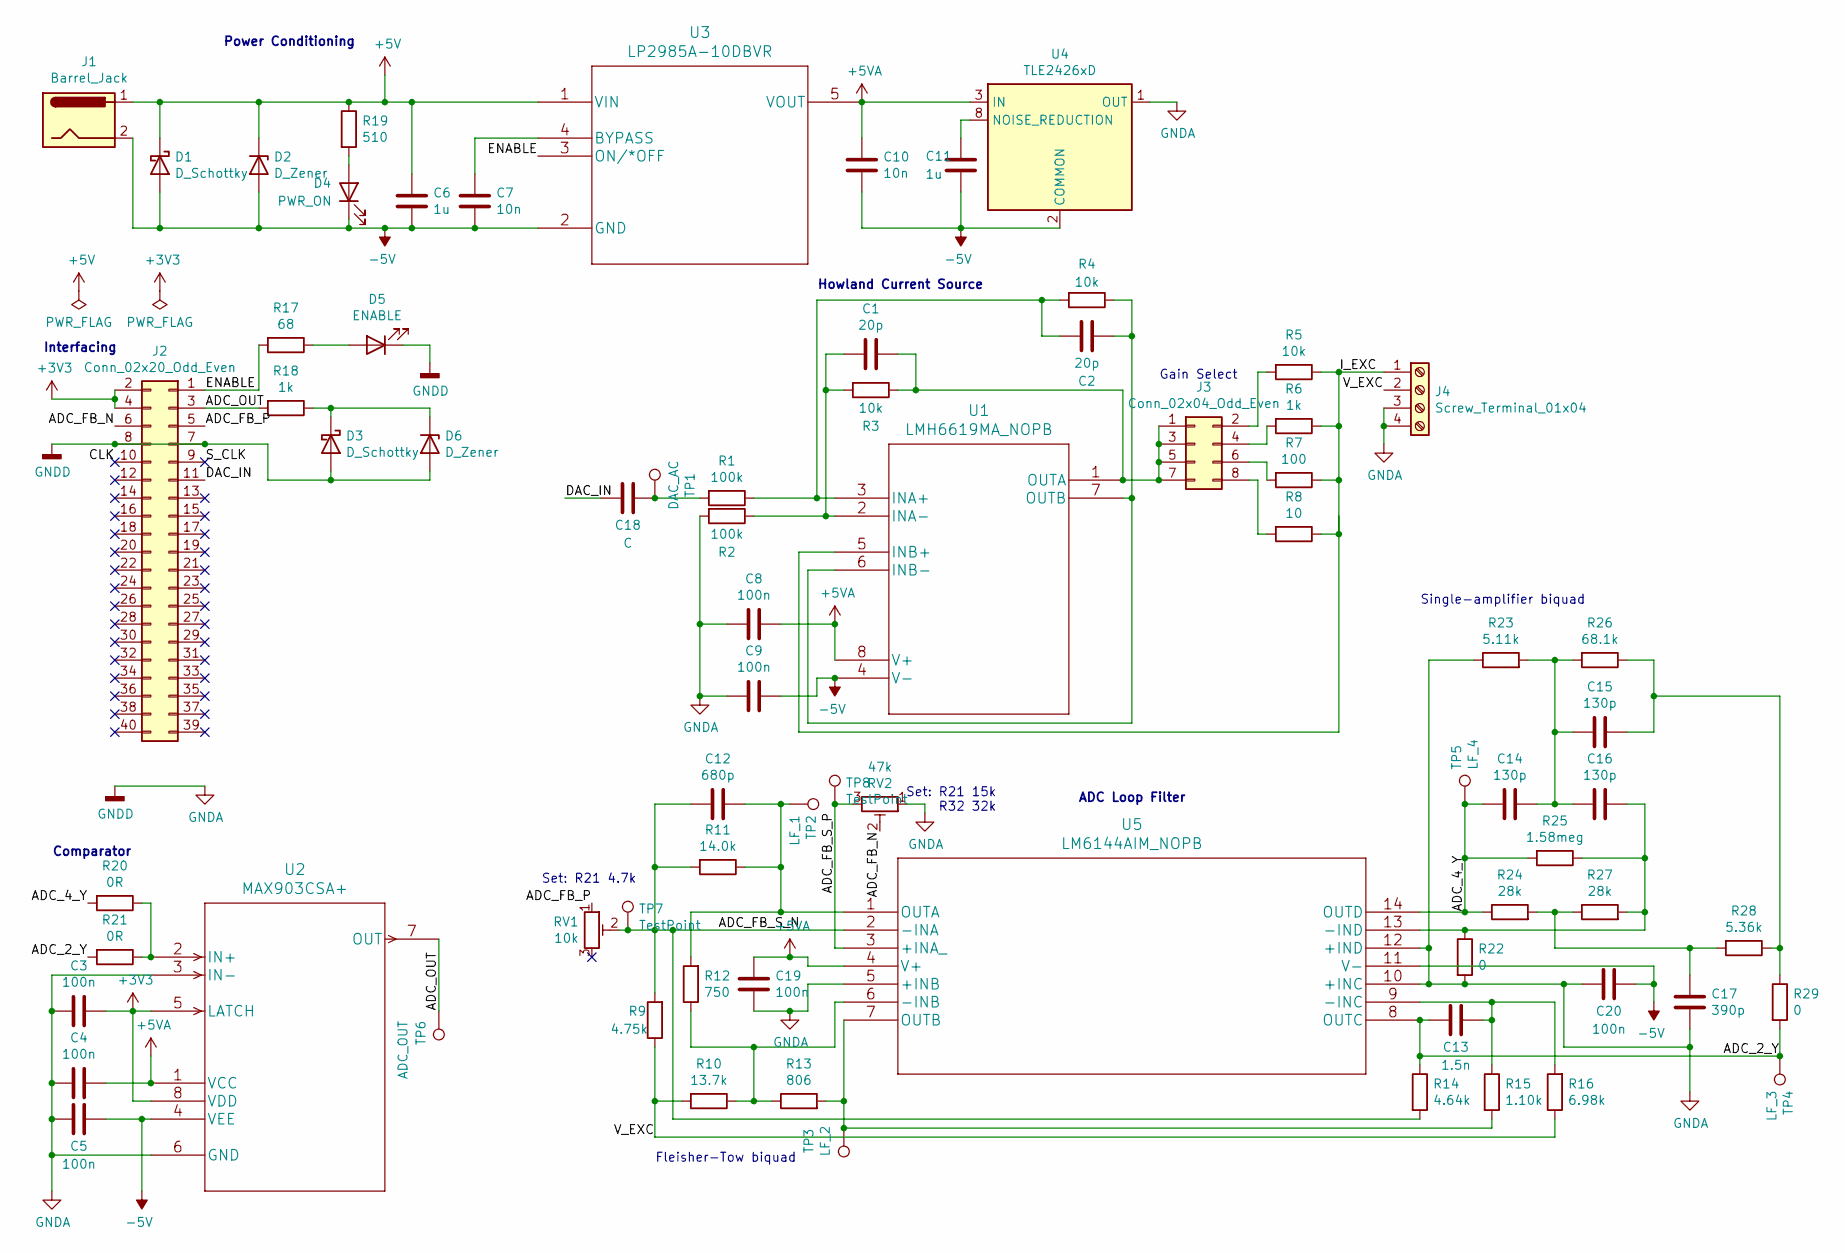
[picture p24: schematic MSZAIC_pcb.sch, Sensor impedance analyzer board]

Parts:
C1, C2: 20p; C_1206_HandSoldering
C3, C4, C5, C8, C9, C19, C20: 100n; C_1206_HandSoldering
C6, C11: 1u; C_1206_HandSoldering
C7, C10: 10n; C_1206_HandSoldering
C12: 680p; C_1206_HandSoldering
C13: 1.5n; C_1206_HandSoldering
C14, C15, C16: 130p; C_1206_HandSoldering
C17: 390p; C_1206_HandSoldering
C18: C; C_1206_HandSoldering
D1, D3: D_Schottky; D_1206
D2, D6: D_Zener; D_1206
D4: PWR_ON; LED_1206_HandSoldering
D5: ENABLE; LED_1206_HandSoldering
J1: Barrel_Jack; BARREL_JACK
J2: Conn_02x20_Odd_Even; Pin_Header_Straight_2x20_Pitch2.54mm
J3: Conn_02x04_Odd_Even; Pin_Header_Straight_2x04_Pitch2.54mm
J4: Screw_Terminal_01x04; TerminalBlock_Phoenix_MPT-2.54mm_4pol
R1, R2: 100k; R_1206_HandSoldering
R3, R4, R5: 10k; R_1206_HandSoldering
R6, R18: 1k; R_1206_HandSoldering
R7: 100; R_1206_HandSoldering
R8: 10; R_1206_HandSoldering
R9: 4.75k; R_1206_HandSoldering
R10: 13.7k; R_1206_HandSoldering
R11: 14.0k; R_1206_HandSoldering
R12: 750; R_1206_HandSoldering
R13: 806; R_1206_HandSoldering
R14: 4.64k; R_1206_HandSoldering
R15: 1.10k; R_1206_HandSoldering
R16: 6.98k; R_1206_HandSoldering
R17: 68; R_1206_HandSoldering
R19: 510; R_1206_HandSoldering
R20, R21: 0R; R_1206_HandSoldering
R22, R29: 0; R_1206_HandSoldering
R23: 5.11k; R_1206_HandSoldering
R24, R27: 28k; R_1206_HandSoldering
R25: 1.58meg; R_1206_HandSoldering
R26: 68.1k; R_1206_HandSoldering
R28: 5.36k; R_1206_HandSoldering
RV1: 10k; 23BR50KLFTR
RV2: 47k; 23BR50KLFTR
TP1: DAC_AC; Measurement_Point_Square-TH_Big
TP2: LF_1; Measurement_Point_Square-TH_Big
TP3: LF_2; Measurement_Point_Square-TH_Big
TP4: LF_3; Measurement_Point_Square-TH_Big
TP5: LF_4; Measurement_Point_Square-TH_Big
TP6: ADC_OUT; Measurement_Point_Square-TH_Big
TP7, TP8: TestPoint; Measurement_Point_Square-TH_Big
U1: LMH6619MA_NOPB; LMH6619MA&slash_NOPB
U2: MAX903CSA+; MAX903CSA&plus_
U3: LP2985A-10DBVR
U4: TLE2426xD; TLE2426CD
U5: LM6144AIM_NOPB; LM6144AIM&slash_NOPB

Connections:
+3V3: C3.1, J2.2, J2.4, U2.5 (LATCH), U2.8 (VDD)
+5V: C6.1, D1.1 (K), D2.1 (K), J1.1, R19.1, U3.1 (VIN)
+5VA: C4.1, C8.1, C10.1, C19.1, U1.8 (V+), U2.1 (VCC), U3.5 (VOUT), U4.3 (IN), U5.4 (V+)
-5V: C5.1, C6.2, C7.2, C9.1, C10.2, C11.2, C20.1, D1.2 (A), D2.2 (A), D4.1 (K), J1.2, U1.4 (V-), U2.4 (VEE), U3.2 (GND), U4.2 (COMMON), U5.11 (V-)
/ADC_2_Y: C13.2, R14.1, R21.2, R29.2, TP4.1, U5.8 (OUTC)
/ADC_4_Y: C14.2, R20.2, R24.1, R25.2, TP5.1, U5.14 (OUTD)
/ADC_FB_N: J2.6, RV2.2
/ADC_FB_P: J2.5, RV1.1
/ADC_FB_S_N: C12.2, R9.2, R11.2, R14.2, RV1.2, TP7.1, U5.2 (-INA)
/ADC_FB_S_P: RV2.3, TP8.1, U5.3 (+INA_)
/ADC_OUT: J2.3, R18.2, TP6.1, U2.7 (OUT)
/CLK: J2.10
/DAC_IN: C18.2, J2.11
/ENABLE: J2.1, R17.2, U3.3 (ON/*OFF)
/I_EXC: J4.1, R5.1, R6.1, R7.1, R8.1, U1.5 (INB+)
/S_CLK: J2.9
/V_EXC: J4.2, R9.1, R10.2, R16.1
GNDA: C3.2, C4.2, C5.2, C8.2, C9.2, C17.1, C19.2, C20.2, D3.2 (A), D5.1 (K), D6.2 (A), J2.7, J2.8, J4.3, J4.4, R2.2, R22.2, R23.1, RV2.1, U2.3 (IN-), U2.6 (GND), U4.1 (OUT), U5.5 (+INB), U5.10 (+INC), U5.12 (+IND)
unnamed: C1.1, J3.1, J3.3, J3.5, J3.7, R3.1, U1.1 (OUTA)
unnamed: C1.2, R2.1, R3.2, U1.2 (INA-)
unnamed: C2.1, R4.1, U1.6 (INB-), U1.7 (OUTB)
unnamed: C2.2, R1.1, R4.2, U1.3 (INA+)
unnamed: C7.1, U3.4 (BYPASS)
unnamed: C11.1, U4.8 (NOISE_REDUCTION)
unnamed: C12.1, R11.1, R12.2, TP2.1, U5.1 (OUTA)
unnamed: C13.1, R15.1, R16.2, U5.9 (-INC)
unnamed: C14.1, C15.1, C16.2, R23.2, R26.2
unnamed: C15.2, R26.1, R28.1, R29.1
unnamed: C16.1, R22.1, R25.1, R27.2, U5.13 (-IND)
unnamed: C17.2, R24.2, R27.1, R28.2
unnamed: C18.1, R1.2, TP1.1
unnamed: D3.1 (K), D6.1 (K), R18.1
unnamed: D4.2 (A), R19.2
unnamed: D5.2 (A), R17.1
unnamed: J3.2, R5.2
unnamed: J3.4, R6.2
unnamed: J3.6, R7.2
unnamed: J3.8, R8.2
unnamed: R10.1, R12.1, R13.1, U5.6 (-INB)
unnamed: R13.2, R15.2, TP3.1, U5.7 (OUTB)
unnamed: R20.1, R21.1, U2.2 (IN+)

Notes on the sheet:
Gain Select
Howland Current Source
Power Conditioning
Interfacing
Comparator
Single-amplifier biquad
ADC Loop Filter
Fleisher-Tow biquad
Set: R21 15k R32 32k
Set: R21 4.7k

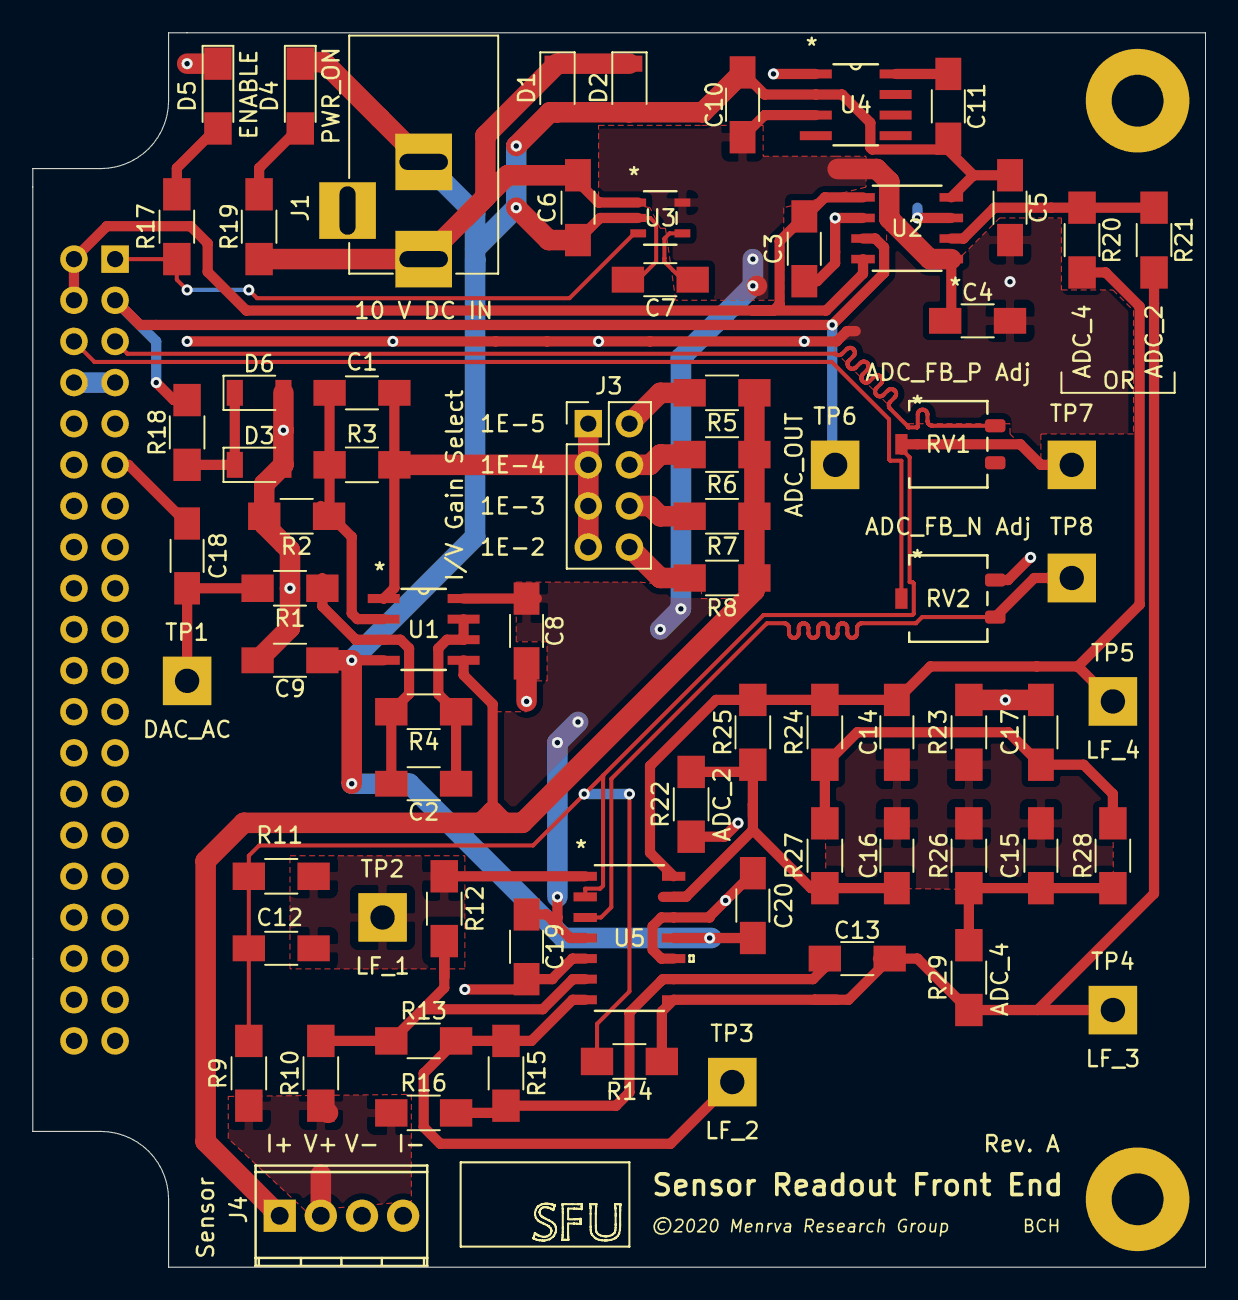
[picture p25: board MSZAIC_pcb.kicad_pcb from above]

Board: 2 copper layers, 72.4 x 76.2 mm, 74 parts (1 on the bottom side), 39 nets.

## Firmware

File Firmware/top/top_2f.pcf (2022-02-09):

###############################################################################

# iCEcube PCF

# Version:            2012.09SP1.22498

# File Generated:     2018-02-15 17:28

# Family & Device:    iCE40HX8K

# Package:            CT256

###############################################################################

### Global Clock

set_io --warn-no-port clk   J3
set_io o_en                 G1

### Switch Inputs

set_io i_sw_rst             P1
set_io i_sw_cal             N3
set_io i_sw_trig            M2
set_io i_sw_aux             L3

### ADC Inputs

set_io i_sclk               H2
set_io i_sd_a               J1
set_io i_sd_b               F1
set_io i_sd_dval            H1

### UART (FTDI Channel B)

set_io i_RS232_RX           B10
set_io o_RS232_TX           B12
set_io RTSn                 B13
set_io CTSn                 A15
set_io DTRn                 A16
set_io DSRn                 B14
set_io DCDn                 B15

### Testing Outputs

set_io o_test[0]            C16
set_io o_test[1]            B16
set_io o_test[2]            D16
set_io o_test[3]            D14

### LED Outputs

set_io o_led[0]             B5
set_io o_led[1]             B4
set_io o_led[2]             A2
set_io o_led[3]             A1
set_io o_led[4]             C5
set_io o_led[5]             C4
set_io o_led[6]             B3
set_io o_led[7]             C3

set_io o_led_en             R1
set_io o_led_busy           P2
set_io o_led_tx             N2
set_io o_led_aux            M1

### DAC Outputs

set_io o_dac                F2

### ADC Outputs

set_io o_adc_en_n           L1
set_io o_adc_zero           K3
set_io o_adc_cal            G2
set_io o_adc_rst            K1
set_io o_sclk               J2

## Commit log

2021-09-29 Add files for Rev. A prototype
    [AFE.xlsx, BOM - Prototype - Passives.xlsx, BOM - Prototype.xlsx, FleischerTow_netlist.sch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]
2021-09-30 Add files for RevB PCB.
    [MSZAIC.kicad_pcb, MSZAIC.sch, Parts.xlsx, SFU-block-logo.dxf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]
2021-10-21 Redefined I/O pins for RevB board
2021-10-21 Enclosure design added.
    [BH1BoardEnclosure.STL, BH2EnclosureBase.STL, BH3EnclosureLid.STL, BH4EnclosureLid.STL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]
2021-11-02 Data readout working with RevB board.
2021-11-02 Readout working with RevB board.
    [Backup of Enclosure.SLDASM, Enclosure.SLDASM, EnclosureLid - EnclosureBase-1.STL, EnclosureLid - EnclosureLid-1.STL]
2022-02-09 top_1f working. Modified sine_lut to separate 1/4-wave logic.
    [Index Calculations for fir_csd_logic_varcoef.xlsx]
2022-04-21 client: multiple channel graphing, thread lock
2022-05-31 Calibration and client changes.
    [Calibration.xlsx, Calibration2.xlsx, Calibration3.xlsx, Calibration4.xlsx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]
2022-06-07 Client: timestamp since trigger, TSV file
    [Log_2022-06-07T181240.tsv]
2022-07-22 Custom model support for client
    [100pF_33kOhm_100kHz_RCparallel.tsv, 100pF_33kOhm_100kHz_raw.tsv, 100pF_33kOhm_12kHz_RCparallel.tsv, 100pF_33kOhm_12kHz_raw.tsv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]
2022-08-08 Fixed error in IQ mode (2)
    [Howland_ds_LMH6619.sch, Log_2022-06-07T181240.tsv, SensReadPCB.sch]
2023-04-11 Version used for paper
    [Backup of Enclosure.SLDASM, Backup of EnclosureBase.SLDPRT, Backup of EnclosureLid.sldprt, Calibration.xlsx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]
2023-04-20 Minor fix to Readme
    [Calibration.xlsx, ExcitationFrequencies.xlsx]

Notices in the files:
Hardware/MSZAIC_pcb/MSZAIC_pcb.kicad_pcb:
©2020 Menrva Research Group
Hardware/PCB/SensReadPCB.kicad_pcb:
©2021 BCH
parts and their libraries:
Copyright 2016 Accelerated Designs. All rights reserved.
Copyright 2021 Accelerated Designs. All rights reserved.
